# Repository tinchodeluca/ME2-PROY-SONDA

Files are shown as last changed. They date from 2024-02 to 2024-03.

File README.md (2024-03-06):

# Cálculo de Permitividad de Materiales mediante una Sonda

Este proceso permite calcular la permitividad relativa (εᵣ) de materiales a partir de la medición de parámetros S11 con un VNA y una sonda. Se adquieren los parámetros de circuito abierto, circuito cerrado y agua destilada como referencia, y luego se miden los parámetros del material a calcular.
___
## Catedra Medidas Electrónicas II - UTN FRBA - 2023 -
>>**Revisión 01**  Fecha: 05/03/2024
***
- **Docente:** Henze Alejandro Martín
- **JTP    :** Geria Juan Manuel
### Alumnos 
- Almude Tupac
- De Luca Martín Alexandro
  
Se partió de trabajos de años anteriores para la misma cátedra que se encuentran [en la siguiente ruta](./01-Bibliografía/Antecedentes%20Soft/Sonda%20Open%20Ended%20-%20Antecedentes).
___
## Contenido

1. [Modelo de Sonda](#modelo-de-la-sonda-utilizada)
2. [Funciones Implementadas](#funciones-implementadas)
    - [Procesamiento de archivos S1P obtenidos del VNA](#procesamiento-de-archivos-s1p-obtenidos-del-vna)
    - [Conversión a Coordenadas Rectangulares](#conversión-a-coordenadas-rectangulares)
    - [Conversión de parámetros S11 a Y11](#conversión-de-parámetros-s11-a-y11)
    - [Submuestreo de S11 (SUBsample_S11)](#submuestreo-de-s11-subsamples11)
    - [Remuestreo de S11 (Resample_S11)](#remuestreo-de-s11-resamples11)
    - [Obtención de Constante Dieléctrica Relativa (εᵣ) del DUT en Medio Agua](#obtención-de-constante-dieléctrica-relativa-εᵣ-del-dut-en-medio-agua)
    - [Obtención de Conductancia en Función de la Frecuencia con el Setup Calibrado](#obtención-de-conductancia-en-función-de-la-frecuencia-con-el-setup-calibrado)
3. [Modelos Teóricos](#modelos-teóricos)
    - [Obtención de Modelo de Debye para Agua Destilada](#obtención-de-modelo-de-debye-para-agua-destilada)
    - [Obtención de Modelo de Constante Dieléctrica para Alcohol Etílico](#obtención-de-modelo-de-constante-dieléctrica-para-alcohol-etílico)
    - [Obtención de Modelo de Constante Dieléctrica para Alcohol Isopropílico](#obtención-de-modelo-de-constante-dieléctrica-para-alcohol-isopropílico)
4. [Ejemplos de Uso](#ejemplos-de-uso)
    - [Procesamiento de Archivos S1P para Medios Específicos](#procesamiento-de-archivos-s1p-para-medios-específicos)
    - [Obtención de Constante Dieléctrica Relativa para Diferentes Medios](#obtención-de-constante-dieléctrica-relativa-para-diferentes-medios)
    - [Procesamiento y Estimación de Constante Dieléctrica Relativa para Resina](#procesamiento-y-estimación-de-constante-dieléctrica-relativa-para-resina)
5. [Proceso de Clonación y Procesamiento en Python](#proceso-de-clonación-y-procesamiento-en-python)
6. [Pasos a Seguir](#pasos-a-seguir)
7. [Resultados](#resultados)
    - [Imágenes de Permitividad Relativa (εᵣ)](#imágenes-de-permitividad-relativa-εᵣ)
        - [Er_Acetona_Medido](#er_acetona_medido)
        - [Er_agua_Teorico](#er_agua_teorico)
        - [Er_AlchEtilico_Teorico](#er_alchetilico_teorico)
        - [Er_AlchIsoprop_Medido](#er_alchisoprop_medido)
        - [Er_AlchIsoprop_Teorico](#er_alchisoprop_teorico)
        - [Er_AlchIsoprop_VS](#er_alchisoprop_vs)
        - [Er_Resina](#er_resina)
___
## Modelo de la Sonda utilizada

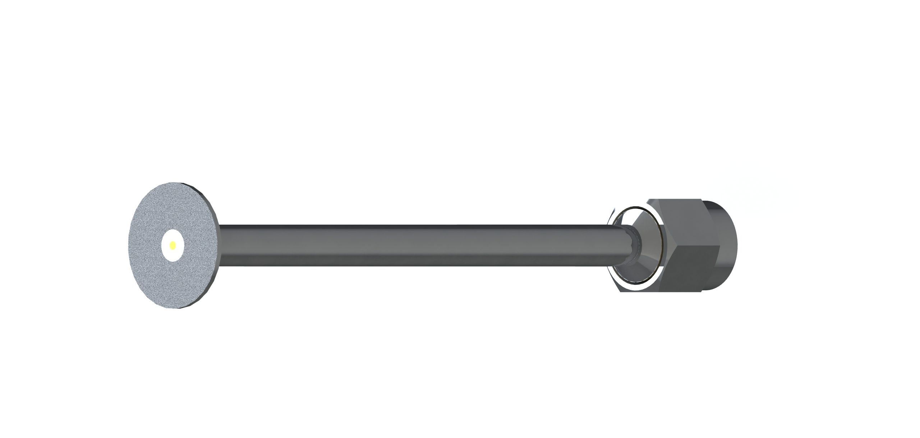
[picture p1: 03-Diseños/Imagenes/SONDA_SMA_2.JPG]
Imagen de la Sonda


Se pueden encontrar los [modelos 3D](./03-Diseños/Sonda/) de la sonda utilizada y las simulaciones en CST con dicha sonda en la [la siguiente carpeta](./04-CST/)
***
# Funciones implementadas
## Procesamiento de archivos S1P obtenidos del VNA
La función `def vna_proc_file(file_path, file_name)` se encarga de procesar los archivos seleccionados y devuelve un diccionario con la información extraída. Los archivos S1P pueden estar en formato de Modulo y Fase o Parte Real e Imaginaria, dependiendo del modo de adquisición del VNA.

- #### Parámetros
    - `file_path:` Ruta del archivo.
    - `file_name:` Nombre del archivo.
- #### Retorno
    Un diccionario con las siguientes claves:
    - `'Date':` Fecha del archivo.
    - `'Data':` Información de las primeras 11 líneas del archivo.
    - `'Index':` Encabezados de las columnas de datos.
    - `'Frec':` Lista de frecuencias extraídas del archivo.
    - `'Complex':` Lista de números complejos correspondientes a los datos procesados.

Si el archivo tiene extensión `.csv`, la función imprimirá un mensaje indicando que el formato CSV no está soportado y retornará sin procesar el archivo.

## Conversión a Coordenadas Rectangulares

La función `def convertir_a_rectangular(modulo_db, fase_grados)` convierte las coordenadas polares (módulo en decibelios y fase en grados) a coordenadas rectangulares.

- #### Parámetros
    - `modulo_db`: Módulo en decibelios.
    - `fase_grados`: Fase en grados.

- #### Retorno
    - Un número complejo en coordenadas rectangulares.

## Conversión de parámetros S11 a Y11

La función `def S11_to_Y11(frec, S11)` convierte los parámetros S11 (coeficiente de reflexión) a parámetros Y11 (parámetros admitancia).

- #### Parámetros
    - `frec`: Frecuencia.
    - `S11`: Coeficiente de reflexión S11.

- #### Retorno
    Un diccionario con las siguientes claves:
    - `'Frec'`: Frecuencia.
    - `'Complex'`: Valor complejo correspondiente a Y11.

Estas funciones proporcionan herramientas esenciales para el procesamiento y análisis de archivos S1P obtenidos del VNA.
## Submuestreo de S11 (SUBsample_S11)

La función `def SUBsample_S11(small_dict, big_dict)` realiza un submuestreo de los datos en `big_dict` para que coincidan con las frecuencias presentes en `small_dict`. La función elimina las frecuencias no presentes en `small_dict` y retorna un nuevo diccionario con el conjunto de datos ajustado.

- #### Parámetros
  - `small_dict`: Diccionario con un conjunto de datos más pequeño.
  - `big_dict`: Diccionario con un conjunto de datos más grande.

- #### Retorno
  Un nuevo diccionario con las siguientes claves:
  - `'Frec'`: Lista de frecuencias ajustadas.
  - `'Complex'`: Lista de números complejos ajustados.

La función imprimirá un mensaje si el diccionario más pequeño no tiene menos elementos que el diccionario más grande.

- #### Ejemplo de uso
  ```python
  result_dict = SUBsample_S11(small_dict, big_dict)
  ```

## Remuestreo de S11 (Resample_S11)

La función `def Resample_S11(smaller_set, data)` realiza un remuestreo de los datos en `data` para que coincidan con las frecuencias presentes en `smaller_set`. La función realiza una interpolación lineal entre los puntos de datos existentes y devuelve un nuevo conjunto de datos con las frecuencias ajustadas.

- #### Parámetros
  - `smaller_set`: Diccionario con un conjunto de datos más pequeño.
  - `data`: Diccionario con un conjunto de datos más grande.

- #### Retorno
  Un nuevo diccionario con las siguientes claves:
  - `'Frec'`: Lista de frecuencias ajustadas.
  - `'Complex'`: Lista de números complejos ajustados.

- #### Ejemplo de uso
  ```python
  resampled_data = Resample_S11(smaller_set, data)
  ```

## Obtener Constante Dieléctrica Relativa (εᵣ) del Dispositivo bajo Prueba (DUT) en Medio Agua

La función `def get_er_DUTm(frecs, S11_medido, S11_agua, S11_aire, S11_corto)` calcula la constante dieléctrica relativa (εᵣ) del Dispositivo bajo Prueba (DUT) en medio acuoso. Se utiliza un modelo de Debye para el agua en la estimación.

- #### Parámetros
    - `frecs`: Lista de frecuencias.
    - `S11_medido`: Parámetro de dispersión medido del DUT.
    - `S11_agua`: Parámetro de dispersión medido en agua.
    - `S11_aire`: Parámetro de dispersión medido en aire.
    - `S11_corto`: Parámetro de dispersión medido en un cortocircuito.

- #### Retorno
    - Valor numérico de la constante dieléctrica relativa (εᵣ) del DUT en medio acuoso.

## Obtener Conductancia en Función de la Frecuencia con el Setup Calibrado

La función `def get_er_setup(frecs, S11_medido, s11_agua, s11_abierto, s11_isopropilico, s11_corto)` calcula la conductancia en función de la frecuencia con el setup calibrado. Se realiza una estimación de la constante dieléctrica relativa del agua y del isopropanol.

- #### Parámetros
    - `frecs`: Lista de frecuencias.
    - `S11_medido`: Parámetro de dispersión medido del DUT.
    - `s11_agua`: Parámetro de dispersión medido en agua.
    - `s11_abierto`: Parámetro de dispersión medido en un circuito abierto.
    - `s11_isopropilico`: Parámetro de dispersión medido en isopropanol.
    - `s11_corto`: Parámetro de dispersión medido en un cortocircuito.

- #### Retorno
    - Lista de valores numéricos que representan la conductancia en función de la frecuencia con el setup calibrado.

Ambas funciones proporcionan herramientas para el análisis de parámetros de dispersión y la estimación de constantes dieléctricas relativas en diferentes entornos.
# Modelos Teóricos
## Obtener Modelo de Debye para Agua Destilada

La función `def get_debye_model(frecs): #Patron agua destilada` devuelve el modelo de Debye para la constante dieléctrica relativa del agua destilada.

- #### Parámetros
    - `frecs`: Lista de frecuencias.

- #### Retorno
    - Lista de valores numéricos que representan la constante dieléctrica relativa del agua destilada en función de la frecuencia.

## Obtener Modelo de Constante Dieléctrica para Alcohol Etílico

La función `def get_er_pat_alc_etilico(frecs)` proporciona el modelo de la constante dieléctrica relativa para el alcohol etílico.

- #### Parámetros
    - `frecs`: Lista de frecuencias.

- #### Retorno
    - Lista de valores numéricos que representan la constante dieléctrica relativa del alcohol etílico en función de la frecuencia.

## Obtener Modelo de Constante Dieléctrica para Alcohol Isopropílico

La función `def get_er_pat_alc_isopropilico(frecs)` devuelve el modelo de la constante dieléctrica relativa para el alcohol isopropílico al 99% según la curva de Debye.

- #### Parámetros
    - `frecs`: Lista de frecuencias.

- #### Retorno
    - Lista de valores numéricos que representan la constante dieléctrica relativa del alcohol isopropílico en función de la frecuencia.

Estas funciones proporcionan modelos para estimar la constante dieléctrica relativa en diferentes medios, lo que puede ser útil en el análisis de parámetros de dispersión en entornos específicos.
## Ejemplos de Uso

#### Procesamiento de Archivos S1P para Medios Específicos

```python
mea_date = '22-02-24'
file_path = './ME2-PROY-SONDA/rsc/' + mea_date + '/'

# files[mea_date][0] #Aire
# files[mea_date][1] #Isopropil
# files[mea_date][2] #Agua destilada
# files[mea_date][3] #Corto circuito
# files[mea_date][4] #Acetona

s11_agua_dest = vna_proc_file(file_path, files[mea_date][2])
s11_short     = vna_proc_file(file_path, files[mea_date][3])
s11_aire      = vna_proc_file(file_path, files[mea_date][0])
s11_isop      = vna_proc_file(file_path, files[mea_date][1])
s11_acetona   = vna_proc_file(file_path, files[mea_date][4])
```

#### Obtener Constante Dieléctrica Relativa para Diferentes Medios

```python
frecs      = s11_agua_dest['Frec']
er_iso     = get_er_DUTm(frecs, s11_isop['Complex'], s11_agua_dest['Complex'], s11_aire['Complex'], s11_short['Complex'])
er_agua    = get_er_DUTm(frecs, s11_agua_dest['Complex'], s11_agua_dest['Complex'], s11_aire['Complex'], s11_short['Complex'])
er_acetona = get_er_DUTm(frecs, s11_acetona['Complex'], s11_agua_dest['Complex'], s11_aire['Complex'], s11_short['Complex'])
```

#### Procesamiento y Estimación de Constante Dieléctrica Relativa para Resina
*(utilizando un set de datos mayor con una calibración de menor tamaño, interpolando y muestreando nuevamente)*

```python
file_path = './ME2-PROY-SONDA/rsc/' + '21-12-23/'
file_name = 'ResinaN.s1p'
s11_resina_temp = vna_proc_file(file_path, file_name)
s11_resina = Resample_S11(s11_acetona, s11_resina_temp)
er_resina  = get_er_DUTm(frecs, s11_resina['Complex'], s11_agua_dest['Complex'], s11_aire['Complex'], s11_short['Complex'])
```

Estos ejemplos ilustran cómo procesar archivos S1P para diferentes medios y calcular la constante dieléctrica relativa en función de la frecuencia para cada medio. Además, se muestra cómo aplicar el proceso a un nuevo conjunto de datos (Resina) utilizando una función de resample para ajustar las frecuencias.
## Proceso de Clonación y Procesamiento en Python

El script Python ubicado en la carpeta **`05-Software`** de este repositorio utiliza Google Colab o Jupyter para realizar un `git clone` del repositorio y procesar los archivos, almacenándolos en una lista. El script se puede encontrar en [este archivo](./05-Software/ME2_PROYECTO_2023.ipynb).

### Descripción del Proceso

1. **Clonación del Repositorio:**
   - El script comienza realizando un `git clone` del repositorio para obtener la última versión de los archivos.

     ```python
     !git clone https://github.com/tinchodeluca/ME2-PROY-SONDA.git
     ```

2. **Procesamiento de Archivos:**
   - Luego, el script explora la carpeta `./ME2-PROY-SONDA/rsc/` y almacena en un diccionario la lista de archivos para cada carpeta.

     *_([la carpeta recursos `rsc`](./rsc/) almacena carpetas con la fecha de medición y dentro de cada una las señales adquiridas oportunamente)_*

     ```python
     file_path = './ME2-PROY-SONDA/rsc/'
     files = {}

     for folder in os.listdir(file_path):
       if os.path.isdir(file_path + '/' + folder ):
         file_names = os.listdir( file_path + '/' + folder + '/' )
         files[folder] = file_names
     ```
## Pasos a Seguir:

1. **Medición de Parámetros de Referencia:**
   - Medir y almacenar los parámetros S11 del **circuito abierto**.
   - Medir y almacenar los parámetros S11 del **circuito cerrado**.
   - Medir y almacenar los parámetros S11 del **agua destilada**.

2. **Procesamiento de Datos de Referencia:**
   - Procesar los archivos S1P de los parámetros medidos para obtener información estructurada.
   - Calcular la constante dieléctrica relativa (εᵣ) para el **circuito abierto**, el **circuito cerrado** y el **agua destilada** utilizando las funciones implementadas.

3. **Medición de Parámetros del Material a Calcular:**
   - Medir y almacenar los parámetros S11 del material cuya permitividad se desea calcular.
   - Almacenar los documentos en la [carpeta de recursos](./rsc/) junto con el resto de señales.

4. **Procesamiento de Datos del Material a Calcular:**
   - Procesar el archivo S1P del material para obtener información estructurada.
   - Calcular la constante dieléctrica relativa (εᵣ) del material utilizando las funciones implementadas.

5. **Resultados y Análisis:**
   - Analizar los resultados obtenidos para determinar la permitividad relativa del material en función de la frecuencia.
   - Documentar y presentar los resultados de manera clara y comprensible.

Este proceso brinda una metodología ordenada y eficiente para calcular la permitividad relativa de materiales mediante una sonda, permitiendo un análisis detallado y una presentación organizada de los resultados.

## Resultados

## Imágenes de Permitividad Relativa (εᵣ)

### Er_Acetona_Medido
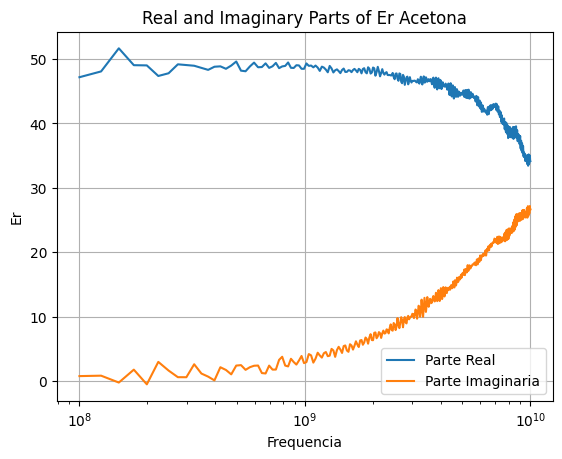
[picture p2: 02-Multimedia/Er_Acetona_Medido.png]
Er_Acetona_Medido


### Er_agua_Teorico
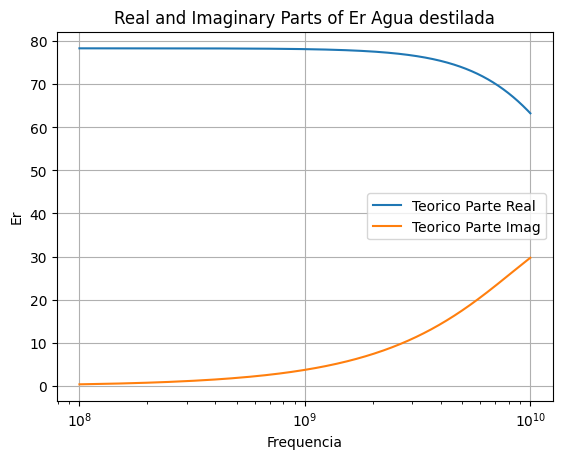
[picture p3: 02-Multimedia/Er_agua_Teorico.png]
Er_agua_Teorico


### Er_AlchEtilico_Teorico
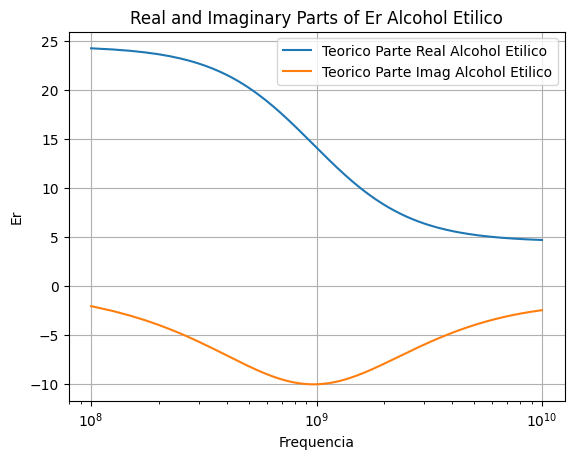
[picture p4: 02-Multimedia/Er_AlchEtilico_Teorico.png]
Er_AlchEtilico_Teorico


### Er_AlchIsoprop_Medido
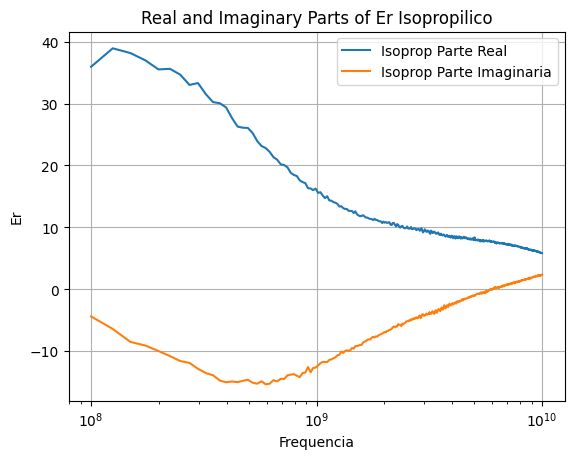
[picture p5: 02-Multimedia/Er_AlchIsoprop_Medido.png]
Er_AlchIsoprop_Medido


### Er_AlchIsoprop_Teorico
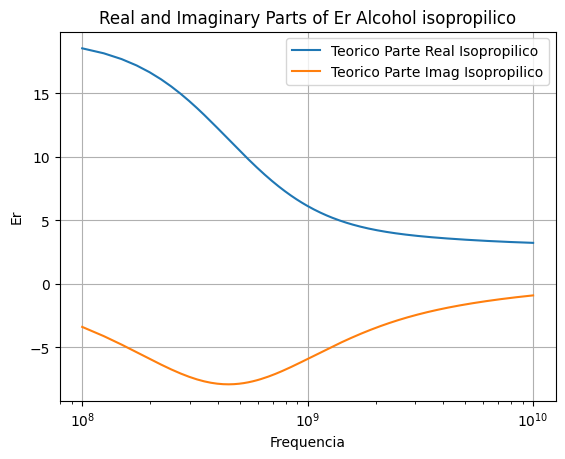
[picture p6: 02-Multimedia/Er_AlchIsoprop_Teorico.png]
Er_AlchIsoprop_Teorico


### Er_AlchIsoprop_VS
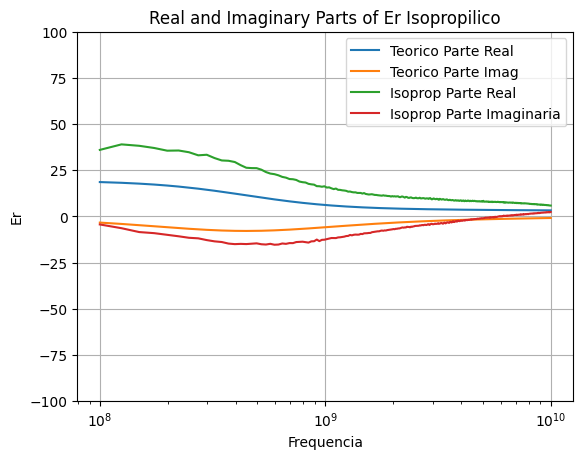
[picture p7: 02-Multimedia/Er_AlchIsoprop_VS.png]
Er_AlchIsoprop_VS


### Er_Resina
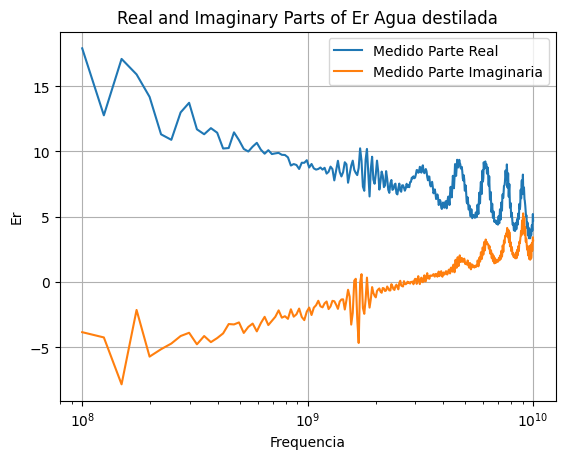
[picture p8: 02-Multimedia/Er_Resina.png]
Er_Resina


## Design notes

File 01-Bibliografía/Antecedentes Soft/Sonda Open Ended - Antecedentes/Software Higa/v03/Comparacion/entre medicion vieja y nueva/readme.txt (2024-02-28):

Comparacion de las mediciones OLD (VNA UTN FRBA) y NEW (VNA INTI)
=================================================================

- Comparacion solo con las temperaturas OLD: 25, 40, 55 y 60.

- Modificacion "." por "," de los archivos .s1p para que el excel interprete correctamente los numeros.

- Eliminacion de la linea de parametros del archivo .s1p.

- Modificacion de rangos:
	- OLD: 100MHz-3GHz (pasos de 50MHz) -> 100MHz-3GHz (pasos de 50MHz y 100MHz a partir del GHz) 
	- NEW: 300kHZ-4GHZ (pasos de 10MHz y 100MHz a partir del GHz) -> 100MHz-3GHz (pasos de 50MHz y 100MHz a partir del GHz)

- Formato de OLD:
	- Frecuencia [Hz]
	- Magnitud s11
	- Fase s11 en grados

- Formato de NEW:
# Hz S RI R 50.000000
	- Frecuencia [Hz]
	- Parametros S
	- Formato: real-imaginario.
	- Resistencia referencia: 50ohm

- Modificacion  del formato de OLD para obtener en vez de magnitud y fase, parte real e imaginaria.

- Modificacion  del formato de NEW para mostrar el formato del numero en tipo general.

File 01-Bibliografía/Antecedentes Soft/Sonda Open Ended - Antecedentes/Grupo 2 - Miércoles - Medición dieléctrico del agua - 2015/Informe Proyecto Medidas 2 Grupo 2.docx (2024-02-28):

UNIVERSIDAD TECNOLÓGICA NACIONAL

FACULTAD REGIONAL BUENOS AIRES

Departamento de Electrónica

Materia: Medidas Electrónicas 2

# Proyecto: MEDICIÓN DE PERMITIVIDAD ELÉCTRICA EN LÍQUIDOS CON PARÁMETROS S

Docente: Ing. Alejandro Henze

Jefe de TP: Ing. Guillermo Monasterios

Ayudante de TP: Ing. Nahir Murana

Grupo N°: 2

Alumnos :

| Apellido y Nombre | Legajo
1 | Das, Ariel | 120.214-5
2 | Cismondi, Luciano | 134.658-1
3 | Grass, Pablo | 111659-9
4 | Higa, Déborah | 143.126-2

Entrega Informe | Fecha | Firma
Primer entrega | / / 12
Aprobación | / / 12

Entrega | Devolución | Re-entrega | Firma Recepción
2° | / / 12 | / / 12
3° | / / 12 | / / 12
4° | / / 12 | / / 12

MEDICIÓN DE PERMITIVIDAD ELÉCTRICA EN LÍQUIDOS CON PARÁMETROS S

Cismondi L., Das A., Grass P., Higa D.

Docente a cargo: Ing. Alejandro Henze

Universidad Tecnológica Nacional - Facultad Regional Buenos Aires

Medidas Electrónicas 2

Resumen: La caracterización de las propiedades dieléctricas de los materiales a frecuencia de radio ha ganado cada vez más importancia, en especial en los campos de investigación en circuitos de microondas, ya que permite obtener resultados del comportamiento eléctrico y/o magnético del material. El siguiente proyecto consiste en la medición de la permitividad eléctrica en líquidos con parámetros S a través de una sonda coaxial.

# 1. INTRODUCCIÓN

La medición de las propiedades dieléctricas implica caracterizaciones de la relación entre la permitividad relativa (εr) y la permeabilidad relativa (μr) de los materiales.

La permitividad dieléctrica se compone de una parte real y una parte imaginaria:

• La parte real, se conoce como constante dieléctrica. Es una medida de la cantidad de energía almacenada en el material, producto de un campo eléctrico externo.

• La parte imaginaria, se conoce como factor de pérdida. Es una medida de la cantidad de energía disipada.

El término tang(ɣ) representa la relación entre la parte imaginaria y la real, llamada tangente de pérdida o factor de disipación[1].

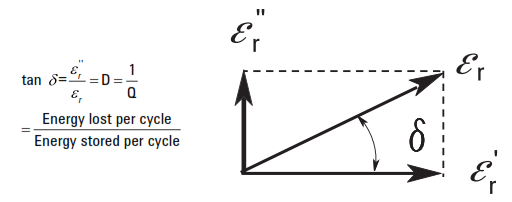
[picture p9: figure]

Fig.1. Representación gráfica del factor de disipación y sus componentes.

La permeabilidad relativa también consta de una parte real, que representa la cantidad de energía almacenada debido a un campo magnético; mientras que la parte imaginaria representa las pérdidas magnéticas del material. La medición de la permeabilidad solo es aplicable a los materiales magnéticos, siendo la mayoría no magnéticos, la permeabilidad es muy cercana a la del espacio libre.

## Distintos métodos de medición

Muchos métodos han sido desarrollados, cada uno se limita a frecuencias específicas, materiales y aplicaciones. El avance de la tecnología ha permitido utilizar programas e instrumentos que facilitan la obtención de los parámetros de transmisión y reflexión. Entre los procedimientos destacados se pueden encontrar: Método de la línea de transmisión/reflexión, método espacio libre, método por resonancia y método por sonda coaxial, siendo este último el utilizado en este proyecto[2].

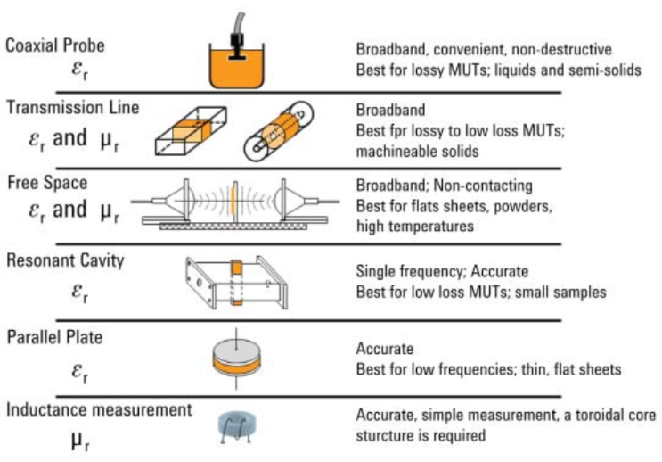
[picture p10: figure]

Fig.2. Distintos métodos y sus aplicaciones.

# 2. DESARROLLO DEL TRABAJO

## Método por sonda coaxial

Ventajas:

• No requiere mecanizado del material bajo ensayo.

• Luego de la calibración, la repetitividad del ensayo es elevada.

• La medición puede realizarse en un ambiente de temperatura controlada.

Desventajas:

• Solo puede medir el parámetro de reflexión.

• Se ve afectada por gaps de aire entre la sonda y la muestra.

El método consiste en la utilización de un cable coaxial como material por donde propagar la señal y se realiza utilizando tres herramientas:

• Vector Network Analyzer (VNA): Realiza la medición del parámetro S11 en función de las frecuencias programadas. Consiste en un generador de señal que excita a una determinada frecuencia al dispositivo bajo prueba (MUT, Material Under Test). El Receptor sintonizado a dicha frecuencia, detecta las señales transmitida y reflejada del MUT y el Display muestra el módulo y la fase de la transmisión y reflexión en función de la frecuencia.

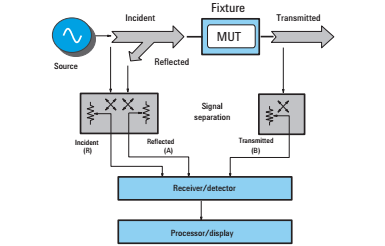
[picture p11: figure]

Fig.3. Setup del VNA utilizado (en nuestro caso, sin medir (B)).

De esta manera, permite la medición de los parámetros S, siendo el de interés el parámetro S11, el coeficiente de reflexión de la tensión del puerto de entrada.

• Sonda: cable coaxial abierto (“open-ended”) utilizado como transductor para la medición de la permitividad de un material. Se llena el coaxial con el material líquido, provocando un cambio en los campos eléctricos y magnéticos en el coaxial y permitiendo así relacionar la medición del parámetro S11 con la permitividad del material.

• Software: convierte el parámetro S11 obtenido de la medición en la permitividad. Se realiza a través de algoritmos iterativos.

## VNA (Vector Network Analyzer)

EL VNA utilizado no era un instrumento stand alone. El mismo fue realizado por los ayudantes de cátedra, y estaba constituido por un generador de RF (Agilent), un osciloscopio (Agilent) y un acopador direcciconal (Agilent).
El generador de RF genera la señal a inyectar por el puerto. El acoplador direccional separara señal incidente y reflejada del puerto del VNA para poder ser medida por dos canales analógicos del osciloscopio.

El control de ambos instrumentos (generación y medición) estaba hecho a través de una computadora, la cual mediante un software codificado en LabView (IDE), generaba los barridos de frecuencia programables, media señal incidente y reflejada, y calculaba mediante procesamiento los parámetros S del puerto.

El sistema descrito fue provisto por la Facultad (UTN FRBA).

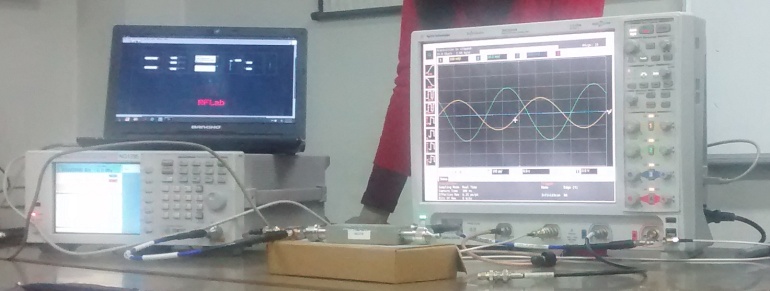
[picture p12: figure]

Fig.4. Vista global del setup VNA.

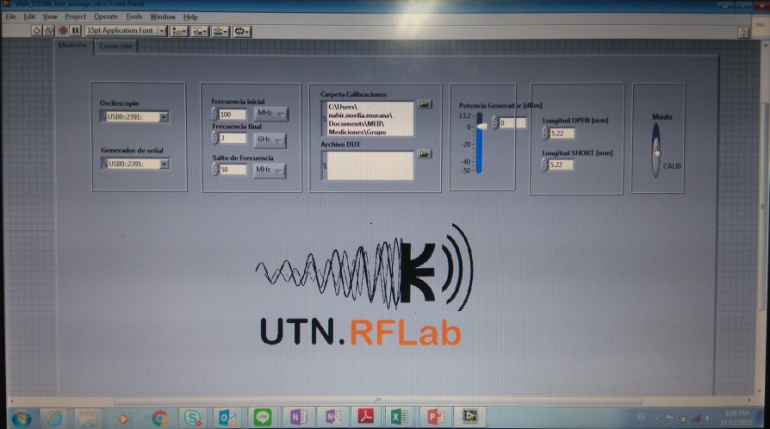
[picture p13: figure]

Fig.5. Vista del control del VNA (IDE LabView)

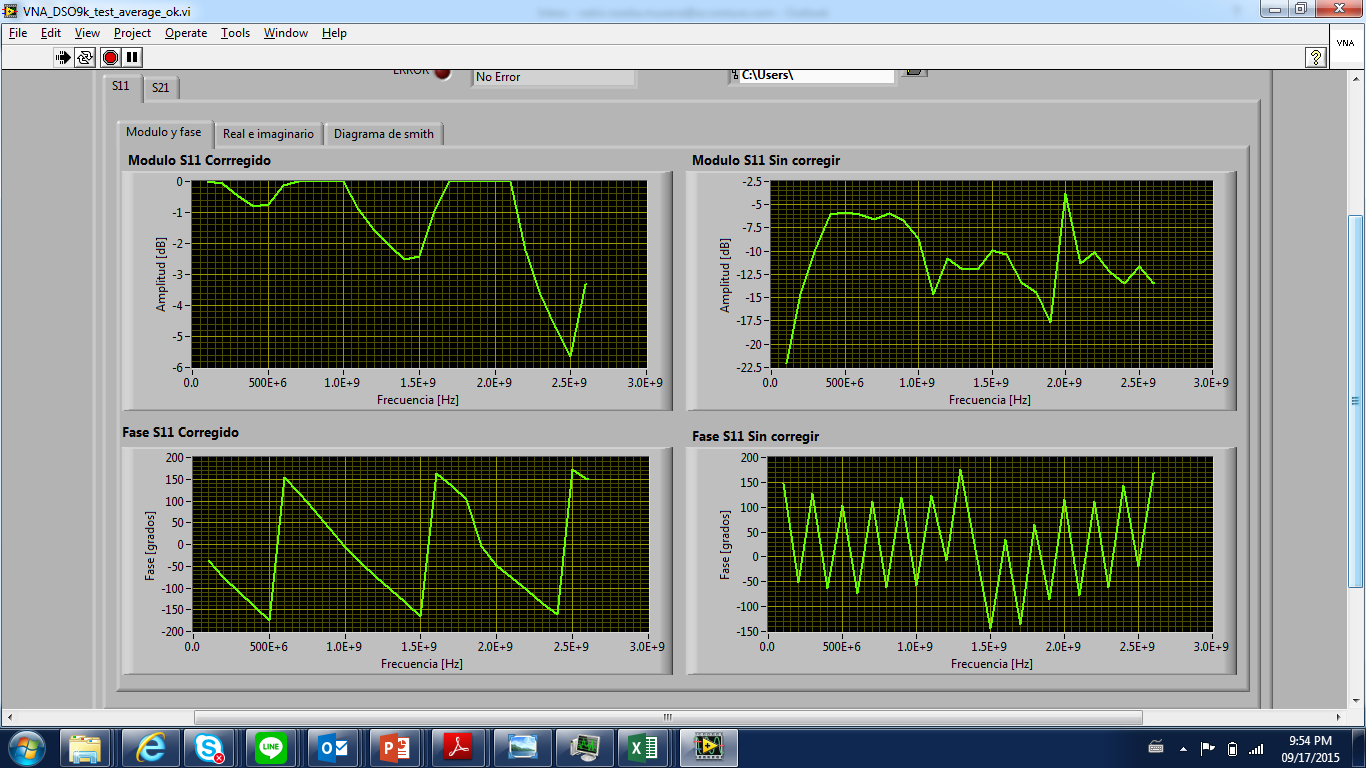
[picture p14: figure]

Fig.6. Pantalla de resultados obtenidos en una medición con el VNA.

## Construcción de la sonda

La mecanización de la sonda se realizó teniendo en cuenta la impedancia característica del sistema a 50Ω con un dieléctrico de aire. Además era primordial prestar atención a la necesidad de poder introducir un líquido dentro de la sonda para que actúe como dieléctrico.

Se construyó una sonda de cobre de un diámetro exterior suficiente para que pueda alojar un conector tipo N en una de sus extremos. Además, la varilla de cobre más fina que se consiguió era de 8mm de diámetro, así que nos fijaba la dimensión “d”, lo que nos deja calcular D:

Zo=1/(2.π.σ).ln(D/d)=(η_0)/(2.π).ln(D/d)

Zo=(120.πΩ)/(2.π).ln((18,4)/8)=50Ω

Otro tema a resolver es que dadas las dimensiones del conector tipo N y su dieléctrico se adaptó el extremo del conducto central al pin central del conector, siempre manteniendo la relación de diámetros para mantener la impedancia característica.

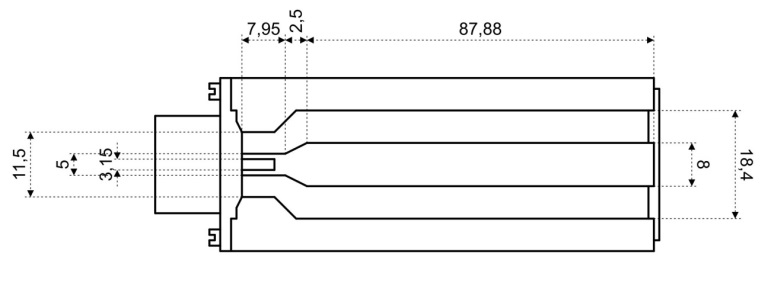
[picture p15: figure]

Fig.7. Plano de la sonda construida [mm].

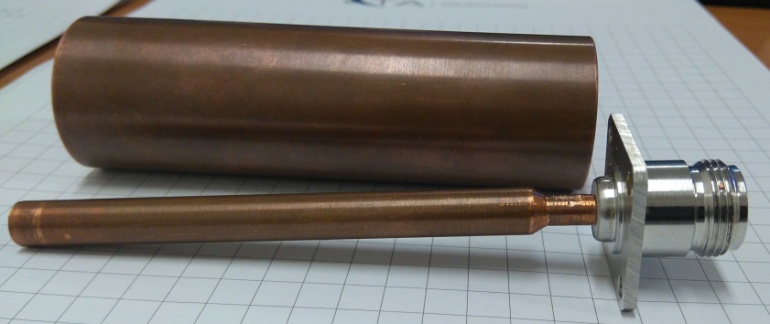
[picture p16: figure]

Fig.8. Vista lateral de los conductores de la sonda.

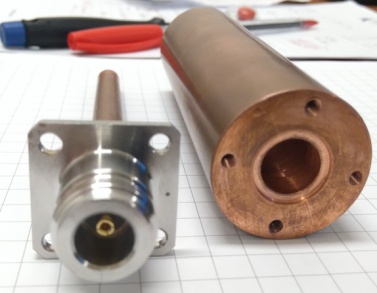
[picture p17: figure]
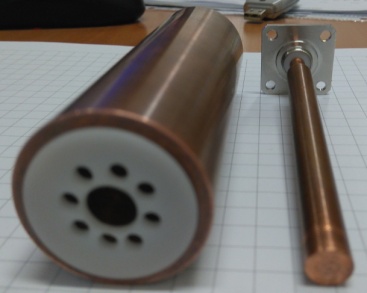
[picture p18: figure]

Fig.9. Vistas posterior e inferior de la sonda.

## Método de conversión

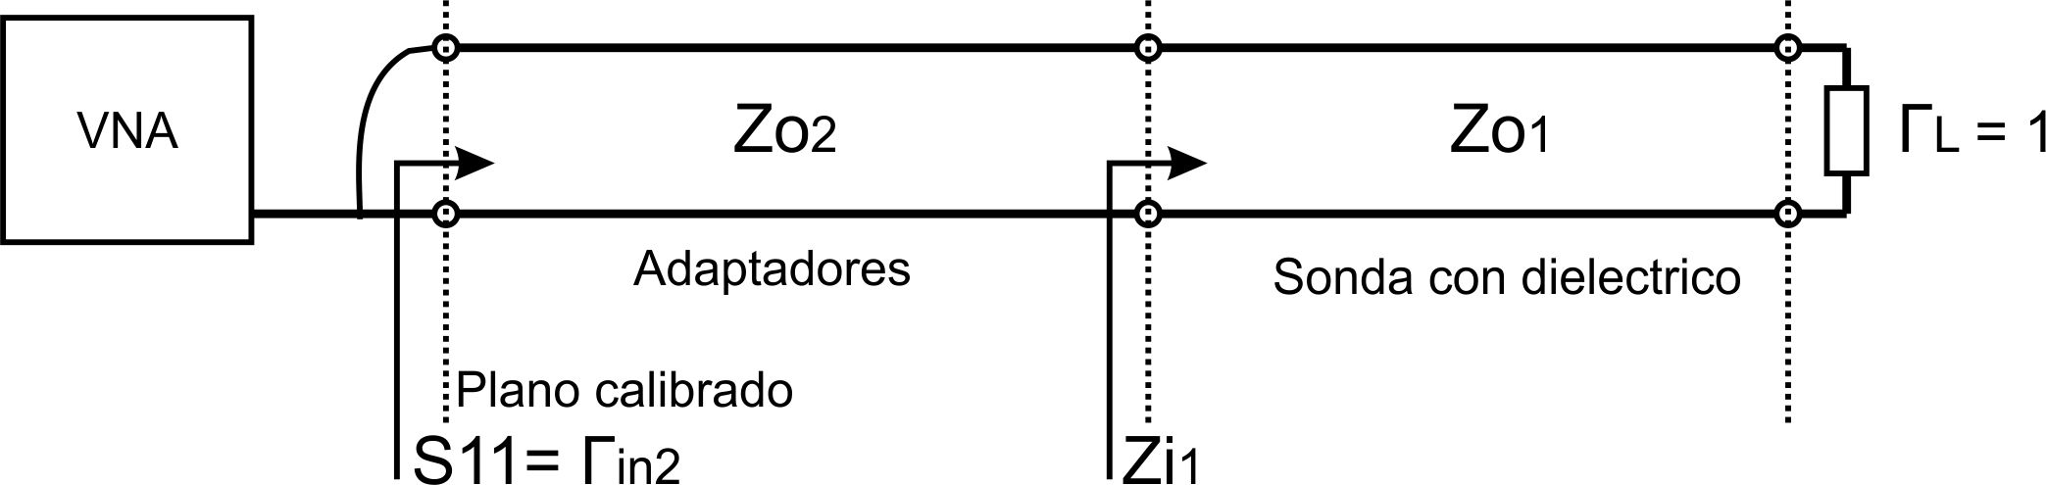
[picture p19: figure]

Fig.10. Setup de medición utilizado.

El plano que figura como “calibrado”, es el punto donde se realizó la calibración del VNA con el método OSM.

Partiendo de la medición del S11:

Γin_2 =s_11

Zi_2 =Zo_2 (1+Γin_2)/(1-Γin_2)

Zi_1 =(j(Zo_2 )^2 .tg(β_2 l_2 )-Zi_2 Zo_2)/(jZi_2 .tg(β_2 l_2 )-Zo_2)

Zi_1 =(1/(2π)√((μ_0)/(ϵ_0 ϵ^(*))).ln⁡(b/a))/(jtg((2π√(ϵ^(*)).f.l_1)/c))

Donde igualando las dos últimas ecuaciones, se puede resolver iterativamente el ϵ^(*) (ya que el mismo esta dentro de una función tangente).

## Resolución de las ecuaciones por software

Nuestra ecuación a resolver es:

0=(1/(2π)√((μ_0)/(ϵ_0 ϵ^(*))).ln⁡(b/a))/(jtg((2π√(ϵ^(*)).f.l_1)/c))-Zi_1

Para resolver la ecuación no lineal de incógnita compleja se utilizó la función fsolve de la librería scipy de Python. También podría usarse la función con el mismo nombre pero de Matlab. Ambas buscan las raíces de una ecuación pero mediante distintos algoritmos: en el caso de Python, utiliza MINPACK’shybrdyhybrj; y en el caso de Matlab, se puede elegir entre tres opciones: 'trust-region-dogleg','trust-region-reflective' y 'levenberg-marquardt'.

fsolve recibe como parámetros obligatorios la ecuación a resolver y un valor estimado de las raíces. Este último parámetro es importante por dos razones:

1) Desde este punto empieza a iterar hasta llegar al resultado, sino a determinada cantidad de iteraciones la función devuelve el último resultado al que llegó e indica que no logró converger.
2) Nuestra ecuación tiene infinitas soluciones. Esto se puede observar desde una perspectiva de una variable donde las soluciones son las intersecciones gráficas entre una tangente y una hipérbola.

Por lo tanto, es importante conocer los valores teóricos y proporcionárselos a la función para que no diverja y para que no caiga en soluciones locales no deseadas. Para ello, recurrimos al modelo de Debye:

ϵ^(*) =ϵ_(∞) +(ϵ_S -ϵ_(∞))/(1+jωτ)

ϵ_(∞) :permitividad relativa a alta frecuencia.

ϵ_S :permitividad relativa a la frecuencia 0 (estática).

τ:tiempo de relajación.

Tanto ϵ_S como τ son inversamente proporcionales a la temperatura. Basándonos en [4] obtuvimos los valores empíricos para cada frecuencia y temperatura del agua destilada, que se detallaran en la parte de mediciones.

# 3. RESULTADOS

## Agua destilada

Fig.11. Comparación tangente de perdida teórica y medida @26º.

Fig.12. Comparación tangente de perdida teórica y medida @40º.

Fig.13. Comparación tangente de perdida teórica y medida @54º.

Fig.14. Comparación tangente de perdida teórica y medida @60º.

Fig.15. Comparación constante dieléctrica teórica y medida @26º.

Fig.16. Comparación constante dieléctrica teórica y medida @40º.

Fig.17. Comparación constante dieléctrica teórica y medida @54º.

Fig.18. Comparación constante dieléctrica teórica y medida @60º.

## Aire

Fig.19. Constante dieléctrica a @26º.

Fig.20. Factor de perdida a @26º.

Fig.21. Tangente de perdida a @26º.

## Alcohol

Fig.22. Constante dieléctrica a @26º.

Fig.23. Factor de perdida a @26º.

Fig.24. Tangente de perdida a @26º.

# 4. DISCUSIÓN

Comparando las mediciones obtenidas, con los valores teóricos calculados, podemos notar tres tendencias significativas.
La primera es que las mediciones tienen un alto valor de dispersión. Consideramos que es debido al error de método de medición (configuración mecánica de la sonda, VNA, agua utilizada) ya que se puede observar que para todas las mediciones a diferentes temperaturas, la forma de los datos en función de la frecuencia se repite sistemáticamente.

La segunda, es que a frecuencias mayores que 1GHz la curva teórica del agua tiende a aumentar, y las mediciones tienen a disminuir.

Esto es debido a la frecuencia de corte de la sonda. Si la calculamos, tomando la fórmula para un cable coaxial y considerando el épsilon del agua y dimensiones de la misma:

f_C _([GHz]) =(190,5)/(√(ε_r)(D+d)_([mm]))=(190,5)/(√81(18,4+8)_([mm]))=0.803[GHz]

Podemos ver que el valor teórico es cercano a la frecuencia donde notamos que la curva empieza a decrecer en vez de subir.

La tercera y más importante, es que a frecuencias comprendidas entre 100MHz y 1GHz y pese a la dispersión, el valor medio de la curva medida, sigue a la curva teórica. Inclusive comparamos el valor medio de la parte real (constante dieléctrica) con valores obtenidos en [5] y resultan bastante similares.
Además, la sonda en su configuración original, tenía un fino anillo de teflón en su punta abierta para mantener la coaxialidad de los conductores. Esto trae aparejado dos problemas. Uno, que en los cálculos teóricos se tomaba como carga de la sonda una carga abierta, sin considerar los problemas de borde para el campo electromagnético. El segundo es que en realidad, dicho anillo de teflón debería considerarse como carga de la sonda, siendo este un capacitor coaxial a calcular y contemplar en los cálculos.

5. CONCLUSIONES

Con respecto a la sonda, fue un buen primer prototipo, pero se debe rediseñarla.

Primero, que la misma tenga un conector tipo N macho, tal cual tienen los patrones OSM que utilizamos y no agregar elementos a la incertidumbre de medición, como ser adaptadores.

Segundo, hay que rediseñar las dimensiones “D y d” de acuerdo a una frecuencia de corte de 3 o 3.5GHz con un ε_r =81 (agua) y que mantenga una Z_o =50Ω para el aire.

Desarrollo:

f_C _([GHz]) =(190,5)/(√(ε_r)(D+d)_([mm])) Zo =60/(√(ε_r))ln(D/d)

Despejando de cada ecuación,

(D+d)_([mm]) =(190,5)/(√(ε_r) f_C _([GHz])) (D/d)=e^((Zo√(ε_r))/60)

(D+d)_([mm]) =K_2 (1) (D/d)=K_1 (2)

K_1 se obtiene calculando y considerando:

Zo=50Ω y ε_r =1 (aire) →K_1 =2,301

Y K_2 lo tenemos que calcular considerando:

f_C _([GHz]) =3.2 y ε_r =81 (Agua), →K_2 =6,6146

Despejando D de (2) y sustituyendo en (1),

K_1 .d+d=K_2 → d(1+K_1 )=K_2 → d=(K_2)/(1+K_1)

en (2)→K_1 (K_2)/(1+K_1)

Finalmente reemplazando los valores calculados de las constantes:

d=2,0038mm y D=4,6108mm

Como se puede observar, las dimensiones son bastante chicas y plantea un desafío mecánico a la hora de construir la sonda.

Tercero, el fino anillo de teflón en su punta abierta para mantener la coaxialidad de los conductores, deberíamos reemplazarlo por un terminador tipo “short” hecho a medida para la sonda (dimensiones y rosca). Esto traería dos ventajas. Una es que el mismo terminador diseñado correctamente sirve como guía para mantener la coaxialidad del sistema. La otra, es que se elimina el anillo de teflón visto como carga, como así el “open” y se reemplaza la carga por un “short”, lo cual es una referencia mucho más precisa.

Igualmente, se concluye que el presente trabajo es un buen avance para demostrar que el método de medición prueba ser útil para caracterizar materiales líquidos donde su preparación en otros métodos convencionales puede ser engorrosa y en algunos casos poco realizables.

# 6. REFERENCIAS

[1] AN 5989-2589EN Agilent Technologies
[2] AN 5991-2171EN Agilent Technologies
[3] Permittivity and Measurements. Komarov, Wang, Tang.
[4] Agilent 85070D, Dielectric Probe Kit Product Overview

IEEE Transactions on instrumentation and measurement, VOL 46 NO 5 October 1997

UTN – FRBA – ME2 Febrero, 2016

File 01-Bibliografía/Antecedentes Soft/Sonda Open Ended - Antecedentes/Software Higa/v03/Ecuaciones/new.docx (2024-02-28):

Γ_(in) =s_11

Z_e =Z_o ((1+Γ_(in) ))/((1-Γ_(in) ))

Z_e =Z_o ([Z_L +jZ_o tan(βx)])/([Z_o +Z_L jtan(βx)])=(Z_o)/(jtan(βx))

Z_o ((1+Γ_(in) ))/((1-Γ_(in) ))=(Z_o)/(jtan(βx))

(1+Γ_(in))/(1-Γ_(in))=1/(jtan(βx))

jtan(βx)=(1-Γ_(in))/(1+Γ_(in))

tan(βx)=-j(1-Γ_(in))/(1+Γ_(in))

βx=tan^(-1) (-j(1-Γ_(in))/(1+Γ_(in)))

β=1/xtan^(-1) (-j(1-Γ_(in))/(1+Γ_(in)))

(2π)/λ=1/xtan^(-1) (-j(1-Γ_(in))/(1+Γ_(in)))

1/λ=1/(2πx)tan^(-1) (-j(1-Γ_(in))/(1+Γ_(in)))

(f√ε)/c=1/(2πx)tan^(-1) (-j(1-Γ_(in))/(1+Γ_(in)))

ε=[c/(2πxf)tan^(-1) (-j(1-Γ_(in))/(1+Γ_(in)))]^2

ε=A^2

A=Btan^(-1) (C)

B=c/(2πxf)

C=-j(1-Γ_(in))/(1+Γ_(in))

jtan(βx)=(1-Γ_(in))/(1+Γ_(in))

jtan((2πxf√ε)/c)-(1-Γ_(in))/(1+Γ_(in))=0

A-B=0

A=jtan((2πxf√ε)/c)

B=(1-Γ_(in))/(1+Γ_(in))

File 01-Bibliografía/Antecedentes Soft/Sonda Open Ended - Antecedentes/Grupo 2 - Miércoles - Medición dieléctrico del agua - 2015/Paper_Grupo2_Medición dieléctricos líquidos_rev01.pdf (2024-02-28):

UTN.BA – Medidas electrónicas II – Año 2015 | 1

Abstract—La caracterización de las propiedades dieléctricas de los materiales a frecuencia de radio ha ganado cada vez más importancia, en especial en los campos de investigación en circuitos de microondas, ya que permite obtener resultados del comportamiento eléctrico y/o magnético del material.

Index Terms— Constante dielectrica, Permititividad, Parametros S, Scattering.

I. INTRODUCCION
a medición de las propiedades dieléctricas implica caracterizaciones de la relación entre la permitividad relativa (εr) y la permeabilidad relativa (μr) de los materiales. La permitividad dieléctrica se compone de una parte real y una parte imaginaria:
- La parte real, se conoce como constante dieléctrica. Es una medida de la cantidad de energía almacenada en el material, producto de un campo eléctrico externo.
- La parte imaginaria, se conoce como factor de pérdida. Es una medida de la cantidad de energía disipada.
El término tang(ɣ) representa la relación entre la parte imaginaria y la real, llamada tangente de perdida o factor de disipación[1].

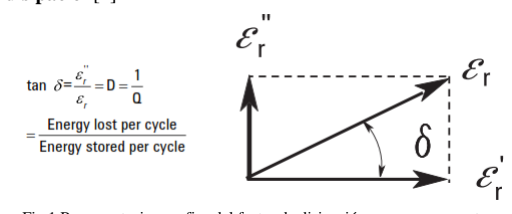
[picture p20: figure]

Fig.1 Representacion grafica del factor de disipación y sus componentes.
La permeabilidad relativa también consta de una parte real, que representa la cantidad de energía almacenada debido a un campo magnético; mientras que la parte imaginaria representa las pérdidas magnéticas del material. La medición de la permeabilidad solo es aplicable a los materiales magnéticos, siendo la mayoría no magnéticos, la permeabilidad es muy cercana a la del espacio libre.

II. DISTINTOS METODOS DE MEDICIÓN Muchos métodos han sido desarrollados, cada uno se limita a frecuencias específicas, materiales y aplicaciones. El avance de la tecnología ha permitido utilizar programas e instrumentos que facilitan la obtención de los parámetros de transmisión y reflexión. Entre los procedimientos destacados se pueden encontrar: Método de la línea de transmisión/reflexión, método espacio libre, método por resonancia y método por sonda coaxial, siendo este último el utilizado en este proyecto[2].

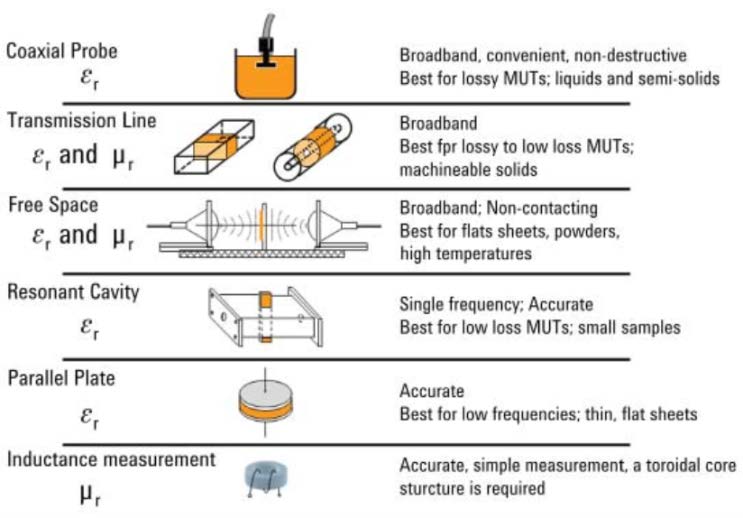
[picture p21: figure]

Fig.2 Distintos métodos y sus aplicaciones.
III. METODO POR SONDA COAXIAL Ventajas:
- No requiere mecanizado del material bajo ensayo.
- Luego de la calibración, la repetibilidad del ensayo es elevada.
- La medición puede realizarse en un ambiente de temperatura controlada.
Desventajas:
- Solo puede medir el parámetro de reflexión.
- Se ve afectada por gaps de aire entre la sonda y la muestra.

El método consiste en la utilización de un cable coaxial como material por donde propagar la señal y se realiza utilizando tres herramientas:

# Medición de permitividad eléctrica en líquidos con parámetros S

Ariel Das, Deborah Higa, LucianoCismondi, Pablo Grass, Alumnos UTN.BA arieldas@hotmail.com, debihiga@gmail.com, cismondil@gmail.com, grass.pablo@gmail.com

L

- Vector Network Analyzer (VNA): Realiza la medición del parámetro S11 en función de las frecuencias programadas. Consiste en un generador de señal que exita a una determinada frecuencia al dispositivo bajo prueba (MUT, Material Under Test). El Receptor sintonizado a dicha frecuencia, detecta las señales transmitida y reflejada del MUT y el Display muestra el módulo y la fase de la transmisión y reflexión en función de la frecuencia.

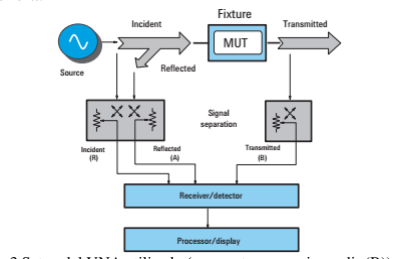
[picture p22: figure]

Fig.3 Setup del VNA utilizado (en nuestro caso, sin medir (B)).
De esta manera, permite la medición de los parámetros S, siendo el de interés el parámetro S11, el coeficiente de reflexión de la tensión del puerto de entrada.
- Sonda: cable coaxial abierto (“open-ended”) utilizado como transductor para la medición de la permitividad de un material. Se llena el coaxial con el material líquido, provocando un cambio en los campos eléctricos y magnéticos en el coaxial y permitiendo así relacionar la medición del parámetro S11 con la permitividad del material.
- Software: convierte el parámetro S11 obtenido de la medición en la permitividad. Se realiza a través de algoritmos iterativos.

IV. CONSTRUCCIÓN DE LA SONDA
La mecanización de la sonda se realizó teniendo en cuenta la impedancia característica del sistema a 50Ω con un dieléctrico de aire. Además era primordial prestar atención a la necesidad de poder introducir un líquido dentro de la sonda para que actúe como dieléctrico.
Contruimos una sonda de cobre de un diámetro exterior suficiente para que pueda alojar un conector tipo N en una de sus extremos. Ademas, la varilla de cobre más fina que conseguimos era de 8mm de diámetro, asi que nos fijaba la dimensión “d”, lo que nos deja calcular D:

# ZZZZ = 1 2. ππ. σσ . ln

DD
dd

= ηη0

# 2. ππ . ln

DD
dd

# ZZZZ = 120. ππΩ 2. ππ . ln

18,4
8 = 50Ω

Otro tema a resolver es que dadas las dimensiones del conector tipo N y su dielectrico adaptamos el extremo de nuestro conducto central al pin central del conector, siempre manteniendo la relación de diámetros para mantener la impedancia caracteristica.


Fig.4 Plano de la sonda construida [mm].

V. MÉTODO DE CONVERSIÓN

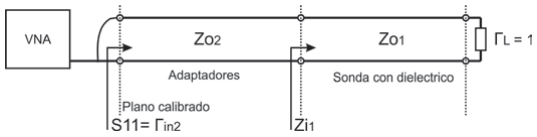
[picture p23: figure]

Fig.5 Setup de medición utilizado.
El plano que figura como “calibrado”, es el punto donde se realizo la calibración del VNA con el método OSM. Partiendo de la medición del S11:

# ΓΓiiii2 = ss11 ZZ 2 = ZZZZ2

# 1 + ΓΓiiii2 1 − ΓΓiiii2 ZZ 1 = jjZZZZ2

2

# .tttt(ββ2ll2) − ZZ 2ZZZZ2 jjZZ 2.tttt(ββ2ll2) − ZZZZ2

ZZ 1 =

1

# 2ππ μμ0 εε0εε∗ . ll ⁡

bb
aa
jj

# 2ππ√εε∗. ff. ll1

cc

Donde igualando las dos ultimas ecuaciones, podemos resolver iterativamente el εε∗ (ya que el mismo esta dentro de

una función tangente).

VI. RESOLUCION DE LAS ECUACIONES POR SOFTWARE
Nuestra ecuación a resolver es:
0 =

1

# 2ππ μμ0 εε0εε∗ . ll ⁡

bb
aa
jj

# 2ππ√εε∗. ff. ll1

cc

− ZZ 1

Para resolver la ecuación no lineal de incógnita compleja se utilizó la función fsolve de la librería scipy de Python. También podría usarse la función con el mismo nombre pero de Matlab. Ambas buscan las raíces de una ecuación pero mediante distintos algoritmos: en el caso de Python, utiliza MINPACK’shybrdyhybrj; y en el caso de Matlab, se puede elegir entre tres opciones: 'trust-region-

## dogleg','trust-region-reflective' y

'levenberg-marquardt'.

fsolve recibe como parámetros obligatorios la ecuación a resolver y un valor estimado de las raíces. Este último parámetro es importante por dos razones:
1) Desde este punto empieza a iterar hasta llegar al resultado, sino a determinada cantidad de iteraciones la función devuelve el último resultado al que llegó e indica que no logró converger.
2) Nuestra ecuación tiene infinitas soluciones. Esto se puede observar desde una perspectiva de una variable donde las soluciones son las intersecciones gráficas entre una tangente y una hipérbola.

Por lo tanto, es importante conocer los valores teóricos y proporcionárselos a la función para que no diverja y para que no caiga en soluciones locales no deseadas. Para ello, recurrimos al modelo deDebye:

# εε∗ = εε∞ +

# εεSS − εε∞ 1 + jjjjjj

εε∞: pppppppp pp aa aa aa ff ff .
εεSS: pppppppp pp aa aa aa ll ff ff 0 ( átt ). :tt dd ó .

Tanto εεSS como son inversamente proporcionales a la

temperatura. Basándonos en [4] obtuvimos los valores empíricos para cada frecuencia y temperatura del agua destilada, que se detallaran en la parte de mediciones.

| VII. MEDICIONES
A. Agua destilada

Fig.6 Comparacion tangente de perdida teorica y medida @26º.

Fig.7 Comparacion tangente de perdida teorica y medida @40º.

Fig.8 Comparacion tangente de perdida teorica y medida @54º.

Fig.9 Comparacion tangente de perdida teorica y medida @60º.

VIII. CONCLUSIÓNES
Comparando las mediciones obtenidas, con los valores teoricos calculados, podemos notar tres tendencias significativas.
La primera es que las mediciones tienen un alto valor de dispersión. Consideramos que es debido al error de método de medición (configuración mecánica de la sonda, VNA, agua utilizada) ya que se puede observar que para todas las mediciones a diferentes temperaturas, la forma de los datos en función de la frecuencia se repite sistematicamente.

La segunda, es que a frecuencias mayores que 1GHz la curva teorica tiende a aumentar, y las mediciones tienen a disminuir. Esto es debido a la frecuencia de corte de la sonda. Si la calculamos, tomando la formula para un cable coaxial:

# ffCC[GGHHHH] = 190,5

# √εε (DD + dd)[ ]

= 190,5
√81(18,4 + 8)[ ]

# = 0.803[GGHHHH]

Podemos ver que el valor teorico es cercano a la frecuencia donde notamos que la curva empieza a decrecer en vez de subir.

La tercera y mas importante, es que a frecuencias comprendidas entre 100MHz y 1GHz y pese a la dispersión, el valor medio de la curva medida, sigue a la curva teorica. Inclusive comparamos el valor medio de la parte real (constante dieléctrica) con valores obtenidos en [5] y resultan
bastante | similares.

Ademas, la sonda en su configuración original, tenía un fino anillo de teflón en su punta abierta para mantener la coaxialidad de los conductores. Esto trae aparejado dos problemas. Uno, que en los cálculos teoricos tomabamos como carga de la sonda una carga abierta, sin considerar los problemas de borde para el campo electromagnetico. El segundo es que en realidad, dicho anillo de teflón debería considerarse como carga de la sonda, siendo este un capacitor

-0.5

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
100 | 1000

Tangente de pérdida

Frecuencia [MHZ]

Agua 26°C (Prom:10,76)

Teórico Agua 26°C

-0.5

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
100 | 1000

Tangente de pérdida

Frecuencia [HZ]

Agua 40°C (Prom:7,36)

Teórico Agua 40°C

-0.5

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
100 | 1000

Tangente de pérdida

Frecuencia [HZ]

Agua 54°C (Prom:5,34)

Teórico Agua 54°C

-0.5

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
100 | 1000

Tangente de pérdida

Frecuencia [HZ]

Agua 60°C (Prom:6,35)

Teórico Agua 60°C coaxial a calcular y contemplar en los cálculos.

Igualmente, concluimos que el presente trabajo es un buen avance para demostrar que el método de medicion prueba ser útil para caracterizar materiales líquidos donde su preparación en otros métodos convencionales puede ser engorrosa y en algunos casos poco realizables.

IX. TRABAJOS FUTUROS
Con respecto a la sonda, fue un buen primer prototipo, pero tenemos que rediseñarla.
Primero, que la misma tenga un conector tipo N macho, tal cual tienen los patrones OSM que utilizamos y no agregar elementos a la incertidumbre de medición, como ser adaptadores.
Segundo, hay que rediseñar las dimesiones “D y d” de acuerdo a una frecuencia de corte de 3 o 3.5GHz con un εε = 81 (agua) y que mantenga una ZZ = 50Ω para el aire.

Tercero, el fino anillo de teflón en su punta abierta para mantener la coaxialidad de los conductores, deberíamos reemplazarlo por un terminador tipo “short” hecho a medida para la sonda (dimensiones y rosca). Esto traería dos ventajas. Una es que el mismo terminador diseñado correctamente sirve como guía para mantener la coaxialidad del sistema. La otra, es que se elimina el anillo de teflón visto como carga, como asi el “open” y se reemplaza la carga por un “short”, lo cual es una referencia mucho mas precisa.

X. REFERENCIAS
[1] AN 5989-2589EN Agilent Technologies
[2] AN 5991-2171EN Agilent Technologies
[3] Permittivity and Measurements. Komarov, Wang, Tang.
[4] Agilent 85070D, Dielectric Probe Kit Product Overview
[5] IEEE Transactions on instrumentation and measurement, VOL 46 NO 5 October 1997

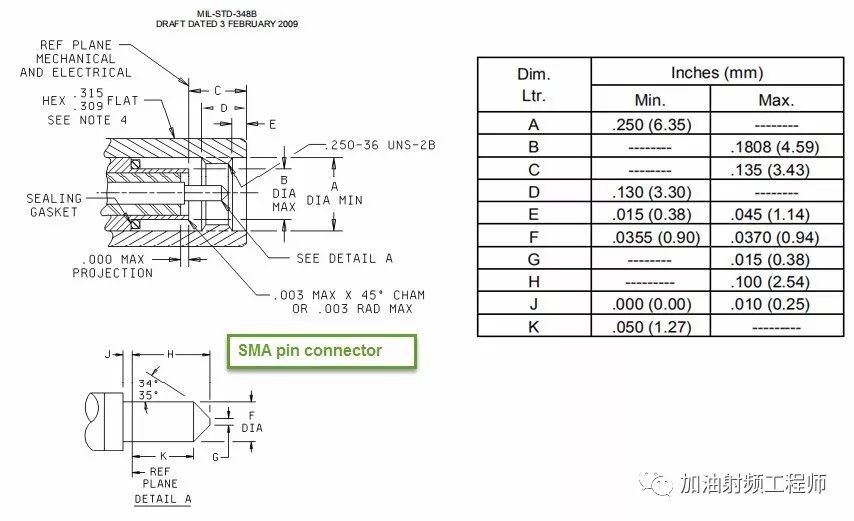
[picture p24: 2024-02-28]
03-Diseños/SMA/MBXY-CR-46d4bd047ff558f94ddf696ebdcfd4d1.png

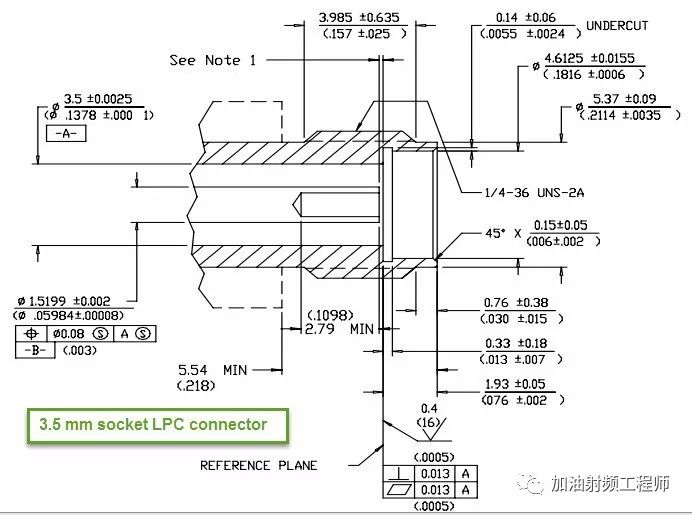
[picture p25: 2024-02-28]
03-Diseños/SMA/MBXY-CR-0249249f3ff1b1c7a5238aef57cc0de9.png

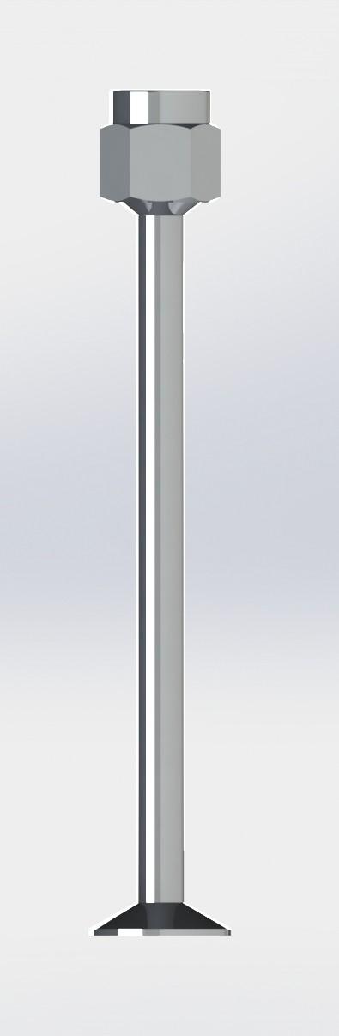
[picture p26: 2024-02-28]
03-Diseños/Imagenes/SONDA_SMA.JPG

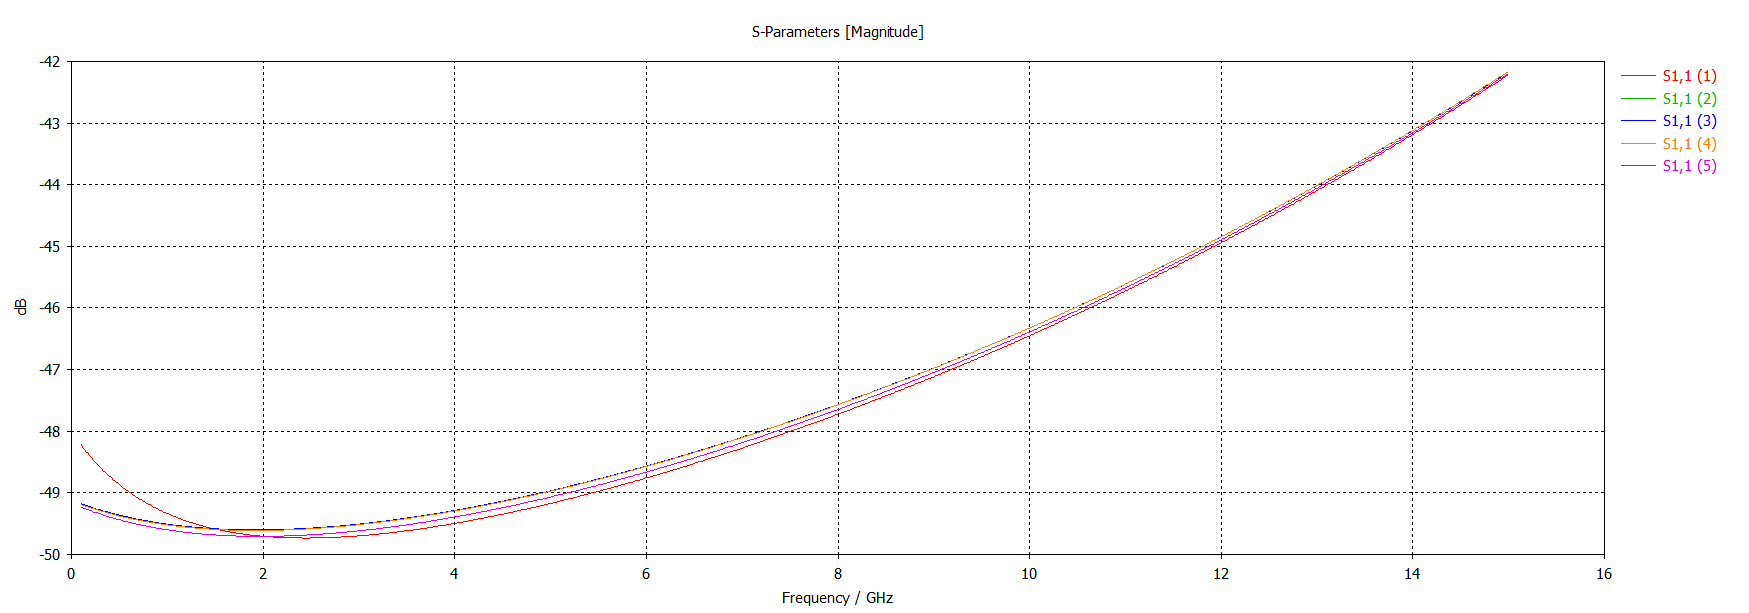
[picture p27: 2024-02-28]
04-CST/Sonda_v2/Temp/clipboard.bmp

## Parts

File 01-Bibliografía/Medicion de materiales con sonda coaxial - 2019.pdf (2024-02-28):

# Informe de proyecto de laboratorio:

# Medici´on de semi-s´olidos con sonda coaxial hasta 18 GHz

# Medidas Electr´onicas II

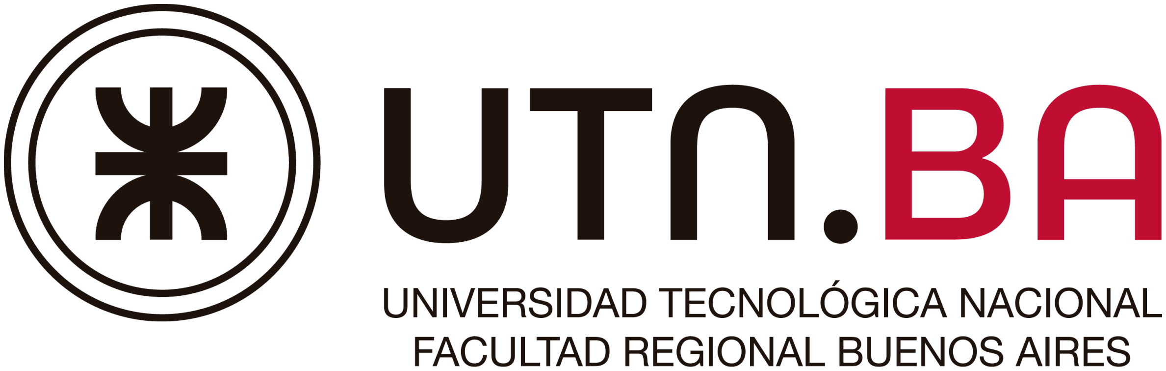
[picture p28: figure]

## Profesor adjunto: Ing. Alejandro Henze Ayudante: Ing. Guillermo Monasterios

Alumnos: Barrios Maximiliano - 149.512-4 Ebrecht Agust´ın - 155.418-2 Fritzler Pablo - 155.413-0 Tucci Federico - 149.827-7

CABA, Argentina, Octubre 2019

## ´Indice

1. Introducci´on | 1
2. Introducci´on del m´etodo | 1
3. Construcci´on de la sonda | 2
3.1. Construcci´on de la primer sonda | | 3
3.2. Construcci´on de la segunda sonda | | 3
4. Software, automatizaci´on y m´etodo detallado | 4
4.1. Automatizaci´on con MatLab | | 4
4.2. Patrones utilizados | | 5
4.2.1. Agua destilada | | 6
4.2.2. Alcohol isoprop´ılico | | 6
5. Corroboraci´on con software y primera medici´on | 7
6. Desarrollo matem´atico | 8
7. Piezas 3D necesarias | 8
8. Mediciones hechas | 9
8.1. Comparaci´on de pieles | | 9
9. Mejoras a futuro | 10
10.Conclusiones | 10
11.Bibliograf´ıa | 11

## 1. Introducci´on

El estudio de las propiedades electromagn´eticas de los materiales org´anicos es de amplio inter´es para diversas disciplinas de la salud y la biolog´ıa. El tejido humano es un material heterog´eneo que contiene agua, mol´eculas org´anicas disueltas, macromol´eculas, iones y materia insoluble. Todos estos elementos est´an organizados en estructuras celulares y subcelulares formando unidades macrosc´opicas y tejidos duros y blandos. La presencia de iones juega un papel importante en la interacci´on con un campo el´ectrico, proporcionando medios para la conducci´on i´onica y efectos de polarizaci´on. La respuesta de toda materia a una onda electromagn´etica viene descrita por las ecuaciones de Maxwell. Seg´un ´estas, aquella depende de los par´ametros intr´ınsecos de la materia: la permeabilidad µ, la permitividad ε y la conductividad σ. La mayor parte de la materia biol´ogica tiene una permeabilidad magn´etica similar a la del vac´ıo µ0, por lo que el an´alisis de su respuesta cuando se excita con frecuencias distintas se centra en la conductividad y en la permitividad relativa a la del vac´ıo. Estos par´ametros constitutivos de la materia proporcionan, por un lado, la capacidad para permitir el movimiento de portadores de carga y, por otro, una medida de su polarizabilidad. En este proyecto se replicaron resultados de mediciones de permitividad relativa para distintos tipos de materiales en un rango de hasta 10GHz, utilizando un VNA (y su respectiva calibraci´on), realizando la medici´on a un puerto (Par´ametro S11) a trav´es de una sonda coaxial.

## 2. Introducci´on del m´etodo

El m´etodo en general consiste en apoyar superficialmente una sonda sobre un tejido, y en base a ciertos c´alculos matem´aticos poder decir la permitividad el´ectrica que tiene, de manera no invasiva y sin procesos traum´aticos, tambi´en de manera muy r´apida.

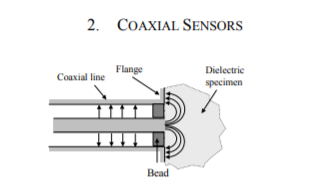
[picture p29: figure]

Figura 1: Principio de funcionamiento de una sonda coaxial.

Para lograr esto se tuvieron que tener que llevar a cabo determinados procesos:

Construcci´on de una sonda

Garantizar el buen funcionamiento de la sonda

Creaci´on de un m´etodo de calibraci´on

Conseguir datos sobre permitividades el´ectricas de ciertos tejidos para poder corroborar las mediciones hechas.

Creaci´on de un software que nos permita automatizar el proceso con el VNA.

Medici´on y comparaci´on de distintos tipos de pieles.

## 3. Construcci´on de la sonda

El primer paso consisti´o en la selecci´on y acondicionamiento de tres cables coaxiales semir´ıgidos, para convertirlos en sondas de medici´on, los cuales fueron provistos por la c´atedra y otros conseguidos en el mercado. El acondicionamiento consisti´o en el cortado, emprolijamiento de la misma y el agregado de una arandela conductora, la cual deb´ıa estar mec´anicamente en el mismo plano que el perteneciente al corte transversal de la sonda.

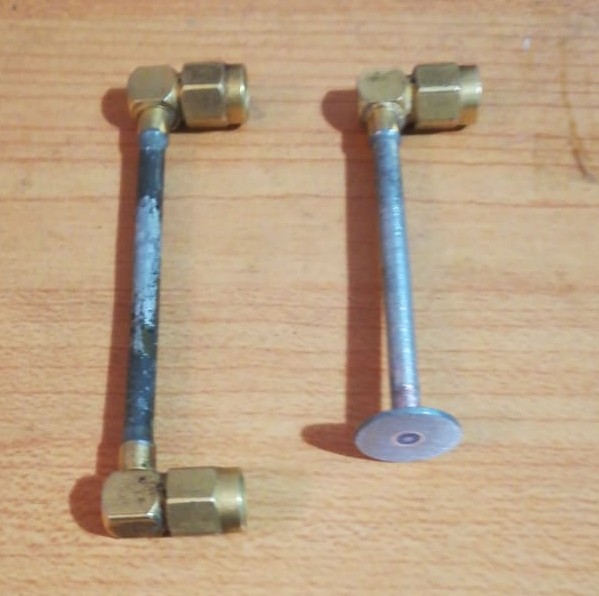
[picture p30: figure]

Figura 2: Sonda antes y despu´es del proceso.

Esta arandela debe captar las ondas electromagn´eticas que se formen en la terminaci´on de la sonda y para ´ verificar su correcto funcionamiento, se realizaron mediciones de corto circuito y circuito abierto, analizando con el VNA para todas las frecuencias de inter´es, que el m´odulo se mantenga constante con valor 1 y la fase sea la correspondiente al CC o CA.

### 3.1. Construcci´on de la primer sonda

La primer sonda se construy´o en base al soldado de la arandela a la sonda, el diagrama de Smith deber´ıa mostrar a circuito abierto un m´odulo de 1 para todas las frecuencias de inter´es, pero revelaron que no se cumpl´ıa:

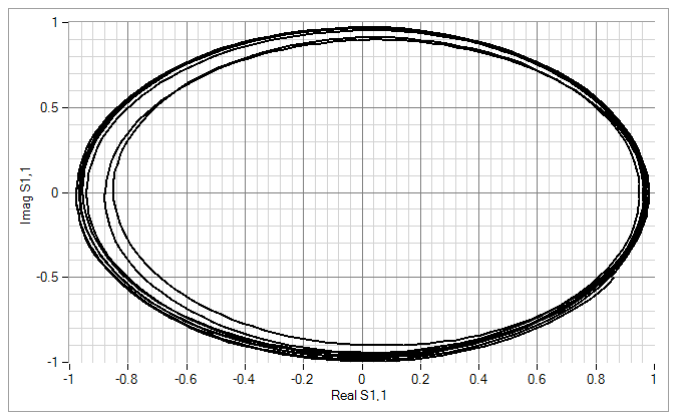
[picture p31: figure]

Figura 3: Diagrama de Smith de VNA tools de la primer sonda.

### 3.2. Construcci´on de la segunda sonda

La segunda sonda se construy´o en base al a˜nadido de la arandela a presi´on con ayuda de pegamento. Las pruebas con el diagrama de Smith del VNA mostraron que fue mejor este m´etodo:

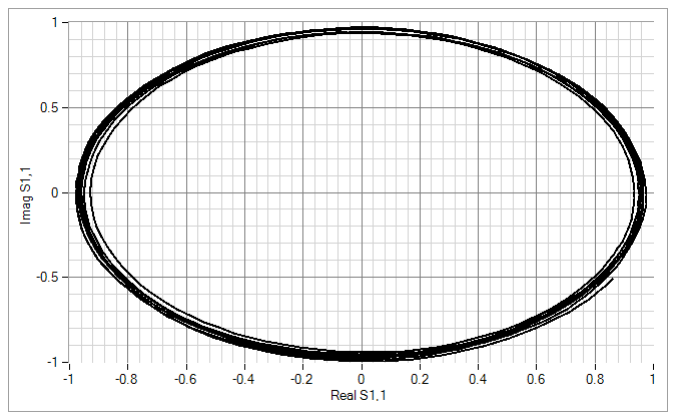
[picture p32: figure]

Figura 4: Diagrama de Smith de VNA tools de nuestra segunda sonda.

## 4. Software, automatizaci´on y m´etodo detallado

### 4.1. Automatizaci´on con MatLab

El segundo paso consisti´o en la automatizaci´on del VNA y el desarrollo de un software en MATLAB que permitiera adquirir las muestras de manera repetitiva y ordenada, as´ı como tambi´en podr´ıamos manejar el VNA con una interfaz gr´afica, realizar la graficaci´on de las se˜nales, almacenamiento de datos, etc.
El primer paso en este proceso fue la creaci´on de los drivers, que constaron en una funci´on de inicializaci´on, una funci´on de desconexi´on y cierre, una funci´on para hacer una medici´on y obtener los datos de la medici´on. La bibliograf´ıa m´as ´util para crear los drivers que comunican a MatLab con el VNA fue el mismo manual de Keysight.

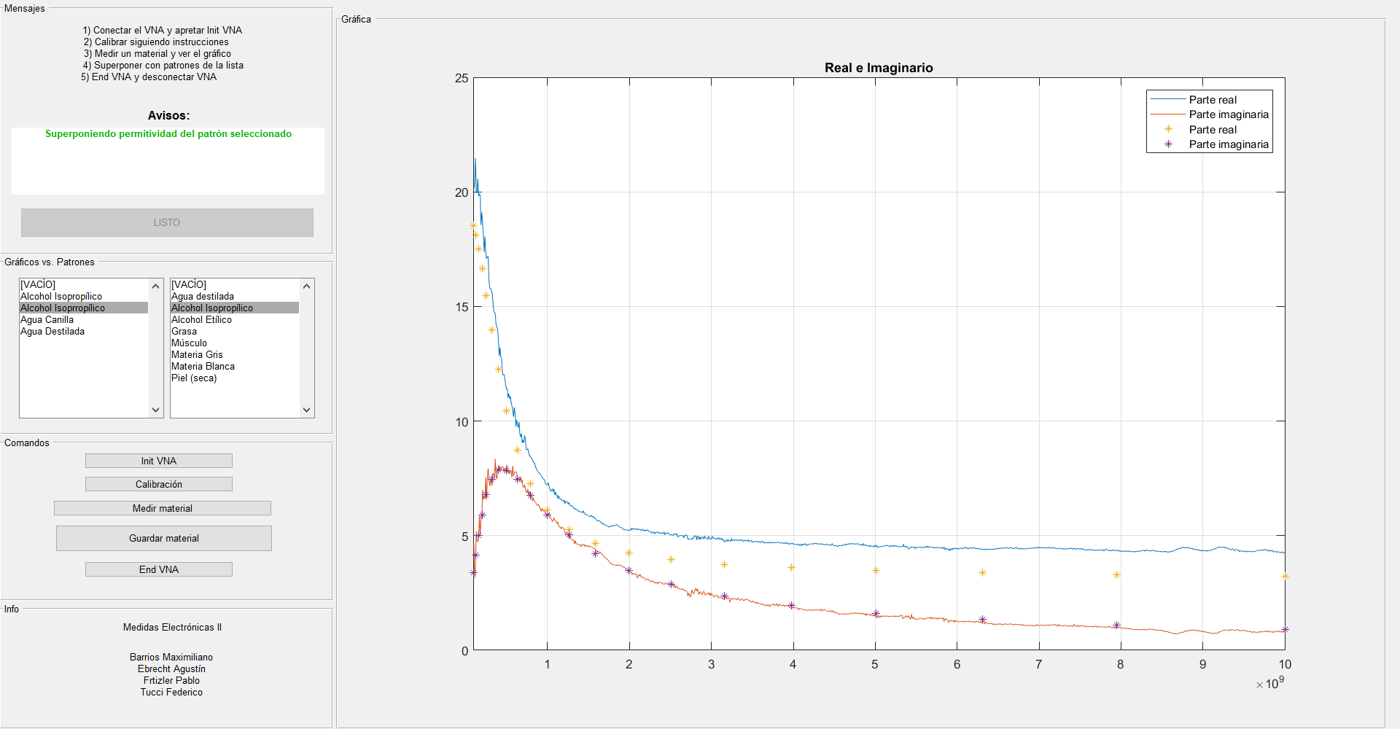
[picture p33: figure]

Figura 5: Programa creado para nuestro prop´osito.

En t´erminos generales, el software desarrollado gu´ıa al usuario en la calibraci´on del equipo, informando los materiales que debe ir colocando para la misma. Posteriormente se puede comenzar con la caracterizaci´on de cualquier material/tejido que se encuentre en contacto superficial con la sonda coaxial.

Deben tenerse en cuenta algunas consideraciones :

La sonda puede oxidarse en caso de estar en contacto con materiales h´umedos, es recomendable realizar una limpieza de la misma luego de cada medici´on y preferentemente con el mismo l´ıquido que se quiera medir posteriormente.

El contacto con la sonda debe ser superficial pero con cierta presi´on, para evitar que las l´ıneas de campo se escapen de la arandela conductora y sean captadas para una correcta medici´on de la onda reflejada.

Los barridos realizados por el VNA disponible en UTN FRBA al d´ıa de la fecha, nos permitieron realizar las mediciones desde los 100 MHz hasta los 10 GHz, sin embargo la sonda podr´ıa utilizarse en principio, hasta los 40 GHz.

Es importante considerar la profundidad de penetraci´on en el caso de l´ıquidos, ya que la onda incidente y reflejadas pueden verse afectadas por el rebote de un contenedor pl´astico/met´alico que puedan modificar el par´ametro S medido.

Las ondas son no ionizantes por lo cual no supone bajo ning´un punto de vista un inconveniente para la interacci´on con tejidos in vivo.

Tambi´en es importante destacar que el software cuenta con una base de datos, en la cual se almacenan curvas patrones (IFAC), las cuales pueden verse en simult´aneo con las mediciones que se est´en tomando para realizar comparaciones entre ambas. La precisi´on de la medici´on no se ve afectada frente a la reducci´on de la cantidad de puntos tomados ( en el eje frecuencial ) por lo que no es necesario despreciar la conductividad para disminuir el tiempo de procesamiento de las muestras, llegando incluso a realizar las mediciones en 30 seg. obteniendo posteriormente el gr´afico en pantalla en otros 30 seg. Tambi´en pueden exportarse las mediciones tomadas en formato s1p, un est´andar en archivos de medici´on de par´ametros S para luego realizar un an´alisis e interpretaci´on de los datos en cualquier software que se desee ( adem´as de VNA Tools ). Es posible tambi´en con algunos ajustes exportarlo a otros formatos, aunque no est´e contemplado en el que aqu´ı se detalla.

### 4.2. Patrones utilizados

Una vez que fue posible comunicarse con el VNA, chequeando el correcto funcionamiento del mismo, se debi´o definir una calibraci´on para luego comenzar con las mediciones. La calibraci´on consiste en un m´etodo similar a OSM, con la diferencia de que en el caso de estudio no cont´abamos con el patr´on de match (impedancia adaptada), por lo que se utilizaron como patrones : cortocircuito, circuito abierto, alcohol et´ılico y agua destilada. Se optaron por estos 4 patrones ya que los primeros dos forman parte de un est´andar, mientras que los otros 2 elementos, son conocidos por diversos estudios en frecuencias de microondas y sus permitividades el´ectricas se encuentran caracterizadas en diferentes curvas.

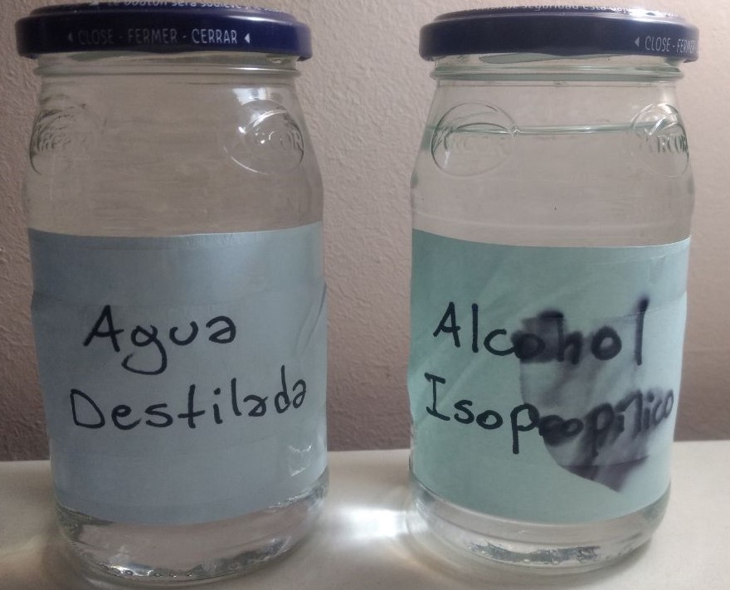
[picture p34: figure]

Figura 6: Frascos en los que se inserta la sonda durante la calibraci´on.

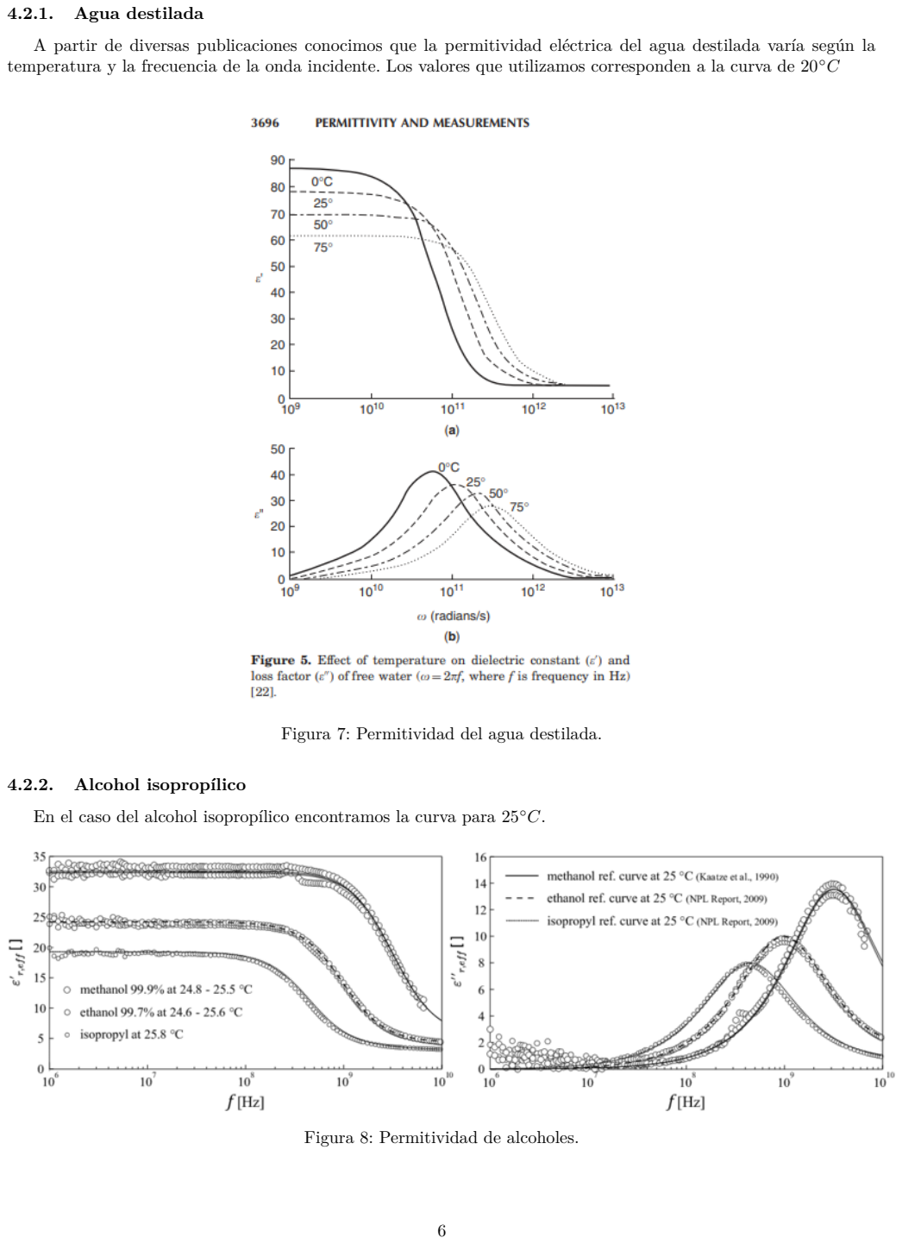
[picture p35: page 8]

### 4.2.1. Agua destilada

A partir de diversas publicaciones conocimos que la permitividad el´ectrica del agua destilada var´ıa seg´un la temperatura y la frecuencia de la onda incidente. Los valores que utilizamos corresponden a la curva de 20◦C

Figura 7: Permitividad del agua destilada.

### 4.2.2. Alcohol isoprop´ılico

En el caso del alcohol isoprop´ılico encontramos la curva para 25◦C.

Figura 8: Permitividad de alcoholes.

## 5. Corroboraci´on con software y primera medici´on

Al llegar a este punto fue fundamental comparar una medici´on de algo conocido junto con su curva te´orica, para esto elegimos medir alcohol isoprop´ılico, dado que era el ´ultimo patr´on utilizado, y para medir no hac´ıa falta retirar la sonda de su ´ultima medici´on.
Los resultados fueron muy satisfactorios:


Figura 9: Alcohol isoprop´ılico medido y comparado con la curva te´orica.

Como se ve en la figura anterior, la curva te´orica se muestra en amarillo y violeta y con el s´ımbolo *. La curva medida se muestra en rojo y azul, la azul comparado con la te´orica tiene un error muy bajo y la roja pr´acticamente es una copia de la te´orica.
El siguiente paso fue medir algo conocido, conociendo la curva te´orica del tejido muscular elegimos medir carne vacuna con resultados tambi´en muy satisfactorios:


Figura 10: Comparaci´on de carne vacuna con tejido muscular.

## 6. Desarrollo matem´atico

Para llegar a la obtenci´on de estas curvas, fue necesario comprender el c´alculo de la permitividad el´ectrica de un material, el cual se compone por una parte real e imaginaria y cuyos valores se pueden obtener a partir de la f´ormula de Debye. La misma consigue caracterizar el εr a partir de la conductancia y la capacidad de la sonda y el material medido, las cuales se estiman a partir de la conversi´on de par´ametros S a par´ametros admitancia, haciendo uso de un modelo de par´ametros concentrados de antena.


Figura 11: Sonda coaxial y modelo de la misma con un tejido.

El proceso matem´atico est´a descripto en el informe “Medici´on de permitividad el´ectricas en l´ıquidos con par´ametros S, Ing. Ariel Das, Ing. Deborah Higa, Ing. Luciano Cismondi, Pablo Grass, Universidad Tecnol´ogica Nacional, Facultad Regional Buenos Aires, Departamento de Ingenier´ıa Electr´onica, 2015”

## 7. Piezas 3D necesarias

Se cre´o un soporte para facilitar la inmovilidad de los cables del VNA y garantizar una mayor calidad de mediciones:


Figura 12: Sonda coaxial en su soporte.

## 8. Mediciones hechas


### 8.1. Comparaci´on de pieles

Figura 13: Diferencia entre las medias de pieles secas y h´umedas.

Estos valores fueron obtenidos de la p´agina italiana http://niremf.ifac.cnr.it/tissprop/htmlclie/htmlclie.php. Los valores que obtuvimos de brazos de varias personas son diferentes a estas curvas te´oricas:

Figura 14: Superposici´on de 11 mediciones diferentes de brazos.

Es importante tener en cuenta que en la “Figura 13” la parte imaginaria se muestra como positiva para facilitar la visualizaci´on en el mismo gr´afico que la parte real. En cambio en la “Figura 14” no est´a este cambio de signo. Se aprecia que en las curvas te´oricas existe una pendiente, negativa en el caso de la parte real, y positiva para la parte imaginaria. En el caso de las mediciones hechas, en promedio, no hay ning´un tipo de pendiente en la parte real, y no tan pronunciada en la parte imaginaria.

## 9. Mejoras a futuro

Como posibles mejoras estamos seguros que el ambiente de medici´on tiene un gran impacto sobre la calidad de la calibraci´on, y por ende, en la calidad de la medici´on que se toma. Las mediciones de piel observadas anteriormente fueron tomadas en una exposici´on de “Feria de proyectos”, con ubicaci´on en la sede Campus, con lo cual la calibraci´on que se hizo en el lugar influy´o mucho en las mediciones tomadas. Conclu´ımos de esto que es fundamental estar en un ambiente controlado y libre de perturbaciones tanto mec´anicas como clim´aticas al momento de calibrar y tomar mediciones.

Creemos tambi´en que hace falta el desarrollo de un m´etodo sistem´atico de medici´on de las pieles, dado que si bien medimos antebrazos, el lugar espec´ıfico siempre vari´o desde la flexura del codo hasta casi la mu˜neca, en la parte anterior tanto como posterior del antebrazo. No conocemos con precisi´on c´omo fueron hechas las mediciones que tomamos como “valores te´oricos” y entendemos que la humedad de la piel, as´ı como otros factores que tambi´en aportan a la permitividad, var´ıan seg´un la zona.

## 10. Conclusiones

Se pudieron obtener mediciones cuya repetibilidad y repetitividad eran representativas tanto para la materia como para un proyecto de investigaci´on. El aprendizaje logrado gracias al proyecto fue motivado tambi´en en parte por la potencialidad de que a futuro, el mismo pueda detectar anomal´ıas como tumores en tejidos de manera no invasiva. Los conocimientos adquiridos se debieron tanto a la parte te´orica pero m´as a´un por poner en pr´actica los conceptos vistos a lo largo de la materia. Esperamos de esta forma, dejar una base para nuevos proyectos o incluso la continuaci´on/extensi´on del mismo.

## 11. Bibliograf´ıa

[1] AN 5989-2589EN Basics of Measuring the Dielectric Properties of Materials, Keysight Technologies, application note.
[2] 5991-2171EN Measuring Dielectric Properties Using Keysight’s Materials Measurement Solutions, Keysight Technologies, application note.
[3] Evaluation of a Reflection Method on an Open-Ended Coaxial Line and its Use in Dielectric Measurements, Prof. Ing. Jan Vrba, CSc., Doc. Ing. Karel Novotn´y, CSc, Czech Technical University in Prague, Faculty of Electrical Engineering, Technick´a 2, 2006.
[4] Medici´on de permitividad el´ectrica en l´ıquidos con par´ametros S, Ing. Ariel Das, Ing. Deborah Higa, Ing. Luciano Cismondi, Pablo Grass, Universidad Tecnol´ogica Nacional, Facultad Regional Buenos Aires, Departamento de Ingenier´ıa Electr´onica, 2015.
[5] http://niremf.ifac.cnr.it/tissprop/htmlclie/htmlclie.php, Institute for Applied Physics ”Nello Carrara”, Florence, Italy, 2012.
[6] Tables of the Complex Permittivity of Dielectric Reference Liquids at Frequencies up to 5 GHz, A.P. Gregory, R.N. Clarke, 2012.
[7] Programaci´on en Matlab del algoritmo de calibraci´on del modelo capacitivo para sondas coaxiales Mar´ıa Garc´ıa Duarte, Escuela T´ecnica Superior de Ingenier´ıa de Telecomunicaci´on, Universidad Polit´ecnica de Cartagena 2017.
[8] Permittivity and measurements, V. Komarov, S. Wang, J. Tang, Washington State University, 2005.
[9] Permittivity measurements using coaxial probes, A Degree Thesis Submitted to the Faculty of the Escola T`ecnica d’Enginyeria de Telecomunicaci´o de Barcelona Universitat Polit`ecnica de Catalunya by Bartomeu Oliver Riera,
B. Riera, May 2016.
[10] Artificial Human Phantoms: Human proxy in testing microwave apparatus that have electromagnetic interaction with the human body, A. T. Mobashsher, A. M. Abbosh, School of ITEE, The University of Queensland St. Lucia, Brisbane QLD 4072, Australia, 2015.
[11] NIST Technical Note 1554, Characterization of Tissue-Equivalent Materials for High-Frequency Applications (200 MHz to 20 GHz), Jannes Baker-Jarvis, Sung Kim, Luke E. Schallinger, Justin Johnson, Brad Givot, 2010.

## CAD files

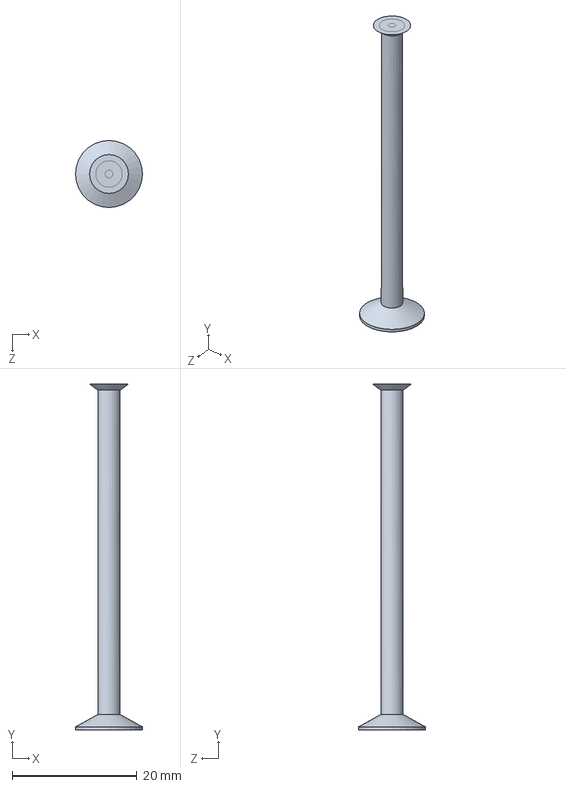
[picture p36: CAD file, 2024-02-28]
03-Diseños/Sonda/Sonda_v1.SLDPRT
10.8 x 55.5 x 10.8 mm

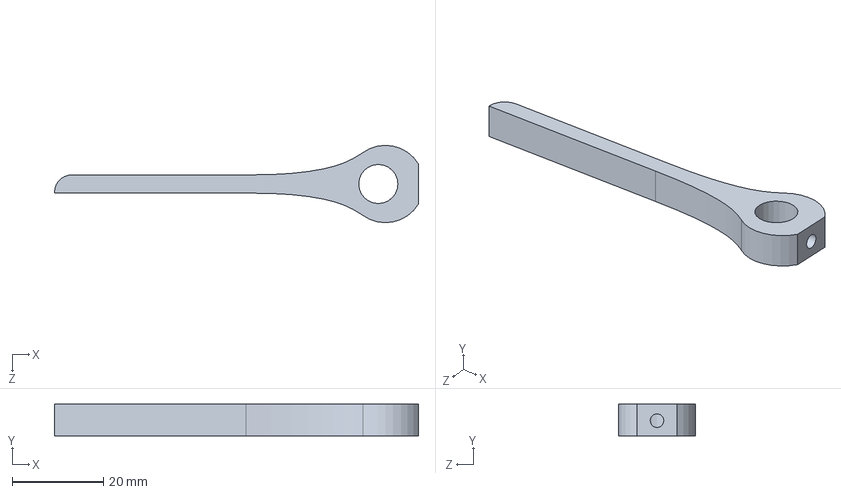
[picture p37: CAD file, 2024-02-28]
03-Diseños/Soportes_onda/Part1.SLDPRT
80.0 x 7.00 x 17.0 mm

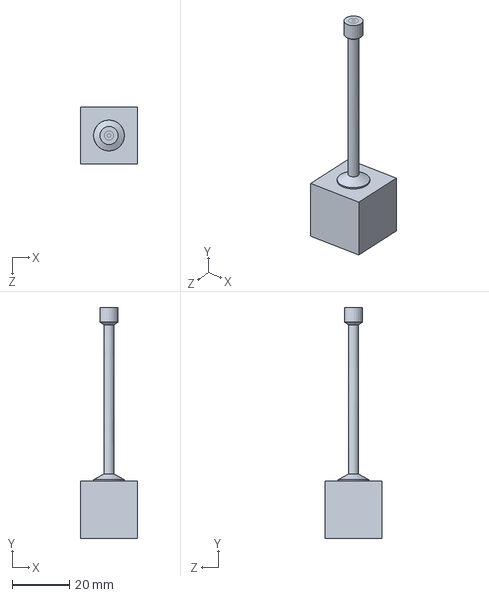
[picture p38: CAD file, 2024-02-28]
04-CST/modelo_sonda/Temp/Node012/Model/3D/Sonda_v2_2.SLDPRT
20.0 x 80.6 x 20.0 mm

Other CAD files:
03-Diseños/SMA/Dielectric.sldprt
04-CST/modelo_sonda/Model/3D/Sonda_v2_1.SLDPRT
04-CST/modelo_sonda/Temp/Node009/Model/3D/Sonda_v2_1.SLDPRT
04-CST/modelo_sonda/Temp/Node010/Model/3D/Sonda_v2_1.SLDPRT
04-CST/modelo_sonda/Temp/Node011/Model/3D/Sonda_v2_1.SLDPRT
04-CST/modelo_sonda/Temp/Node019/Model/3D/Sonda_v2_1.SLDPRT
04-CST/modelo_sonda/Temp/Node020/Model/3D/Sonda_v2_1.SLDPRT
04-CST/modelo_sonda/Temp/Node021/Model/3D/Sonda_v2_1.SLDPRT
03-Diseños/SMA/Gasket.sldprt
03-Diseños/SMA/Key.sldprt
03-Diseños/SMA/Nut.sldprt
03-Diseños/SMA/Pin.sldprt
03-Diseños/SMA/SMA_male_edge_6.5x6.5.SLDASM
03-Diseños/SMA/SMA_male_edge_6.5x6.5.SLDDRW
03-Diseños/SMA/SMA_male_edge_6.5x6.5.STEP
03-Diseños/SMA/SMA_male_edge_6.5x6.5.STL
03-Diseños/SMA/Sleeve.sldprt
03-Diseños/Sonda/Sonda+SMA.STEP
03-Diseños/Sonda/Sonda_v1.SLDDRW
03-Diseños/Sonda/Sonda_v2.SLDPRT
03-Diseños/Sonda/Sonda_v3.SLDPRT
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

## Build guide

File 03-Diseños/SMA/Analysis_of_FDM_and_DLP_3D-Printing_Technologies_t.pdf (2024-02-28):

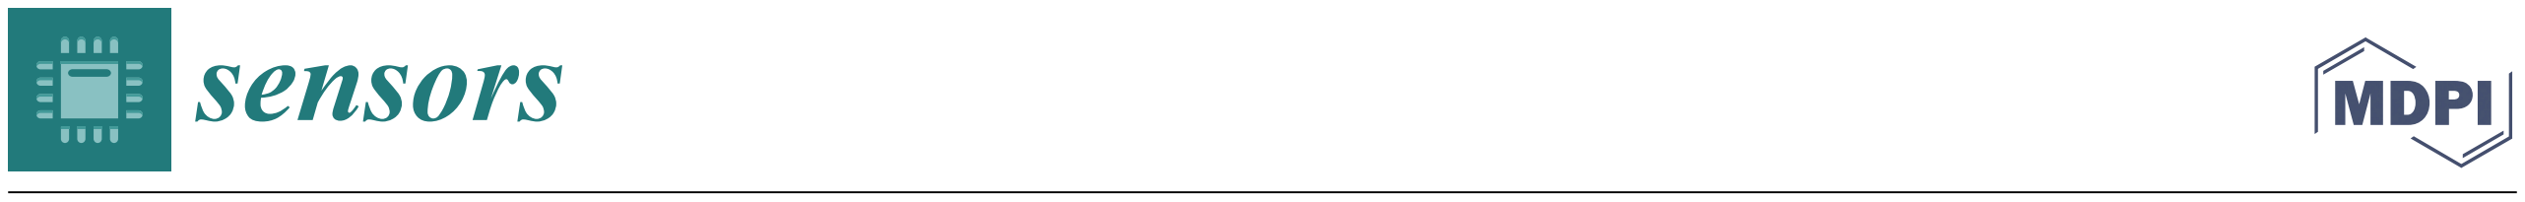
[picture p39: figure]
sensors

Article

# Analysis of FDM and DLP 3D-Printing Technologies to Prototype Electromagnetic Devices for RFID Applications †

Riccardo Colella 1

, Francesco Paolo Chietera 2 and Luca Catarinucci 2,*

(https://www.mdpi.com/1424-8220/21/3/897?type=check_update&version=1)

Citation: Colella, R.; Chietera, F.P.; Catarinucci, L. Analysis of FDM and DLP 3D-Printing Technologies to Prototype Electromagnetic Devices for RFID Applications. Sensors 2021, 21, 897. https://doi.org/10.3390/s21030897 (https://doi.org/10.3390/s21030897)

Academic Editor: Renato Ferrero Received: 7 January 2021
Accepted: 26 January 2021
Published: 29 January 2021

Publisher’s Note: MDPI stays neutral with regard to jurisdictional claims in published maps and institutional affiliations.

Copyright: © 2021 by the authors. Licensee MDPI, Basel, Switzerland. This article is an open access article distributed under the terms and conditions of the Creative Commons Attribution (CC BY) license (https://creativecommons.org/licenses/by/4.0/).

1 | National Research Council of Italy, 73100 Lecce, Italy; riccardo.colella@cnr.it
2 | Innovation Engineering Department, University of Salento, 73100 Lecce, Italy;
| francescopaolo.chietera@unisalento.it
* | Correspondence: luca.catarinucci@unisalento.it
† This paper is an extended verision of our previously published paper “R. Colella, F. P. Chietera and
L. Catarinucci, Digital Light Processing as One of the Promising 3D-Printing Technologies in
| Electromagnetics: Application on RFID”. In Proceedings of the 2020 5th International Conference on Smart
| and Sustainable Technologies (SpliTech), Split, Croatia, 23–26 September 2020, pp. 1–4.

Abstract: In this work, the application in Radiofrequency Identification (RFID) of different additive manufacturing (AM) 3D-printing technologies is discussed. In particular, the well-known Fused Deposition Modeling (FDM) technology is compared with the promising Digital Light Processing (DLP), which is based on the photopolymerization of liquid resins. Based on the research activity of the authors on this topic, a brief introduction to the fundamentals of 3D-printing in electromagnetics as well as to the different applications of both FDM and DLP in realizing Radio Frequency (RF) devices, is firstly given. Then, a comparison of the two technologies is deeply faced. Finally, after evaluated the rugosity of substrates produced with both techniques to verify the potential impact on the design of electromagnetic structures, the two techniques are both exploited for the realization of the dielectric parts of a tunable RFID tag with unconventional shape. It consists of two elements interlinked one each other. The movement between them enables tuning of the resonance frequency as well as the impedance of the antenna. Despite the differences in terms of losses, rugosity, resolution, and dielectric constant, both techniques guaranteed satisfactory values of tag sensitivity, maximum reading range, and tunability. Nevertheless, the careful analysis of the results proposed at the end of the paper suggests how the selection of one technique over the other must be taken considering the specific application constraints.

Keywords: 3D-printing; DLP; FDM; T-Resonator; 3D-printed antennas; UHF; RFID

### 1. Introduction

3D printing by additive manufacturing (AM) is proving to be a promising technology to create high-detailed models wasting less time and spending fewer resources than traditional methods. In the last few years, the advent of more and more accurate and affordable 3D printers has considerably stimulated the electromagnetic community, strongly interested in the realization of microwave components and antennas which take advantage of versatility, cost-effectiveness, and ease of use of these rapid prototyping techniques. Different 3D-printing technologies can be used to produce electromagnetic devices [1–11]. In Farooqui et al. and Fenn et al. [1,2], the Fused Deposition Modelling (FDM) technology has been used to build a cross-polarized (CP) microstrip fed patch antenna in Farooqui et al. [1] and a conformal antenna array in Fenn et al. [2], respectively. In the former case, the conductive parts have been obtained using copper adhesive tape, while in the latter a copper electroplating process has been carried out. In Heirons et al. and Mirmozafari et al. [3,4] a CP patch antenna and a linear array have been described as well, but this time the adopted manufacturing technology has been the Stereo Lithography (SLA) 3D-printing. In these cases, the conductive parts have been realized with inkjet

Sensors 2021, 21, 897. https://doi.org/10.3390/s21030897 | https://www.mdpi.com/journal/sensors

Sensors 2021, 21, 897 | 2 of 13

printing in Heirons et al. [3] and with an electroplating process in Mirmozafari et al. [4]. In Kaddour et al. [5], a Selective Laser Sintering (SLS) process has been used to polymerize polycarbonate (PC) and ABS in other to develop a dual-polarized unidirectional wideband antenna, with metallic parts obtained with electroplating. In Gjokaj et al. [6], a Vivaldi antenna operating in the Ku band has been described as well as its manufacturing process, the so-called Polyjet 3D-printing. In this case, the metallization has been created with a first deposition by sputtering of a Titanium and Copper compound, then used as a base for an electroplating process. A different approach has been described in Jammes et al. [7], where a Jet Metal printing process has been used to produce a metal pyramidal horn antenna without the need to successively metalize anything. Similarly, in Reinhardt et al. [8] the production process of a corrugated pyramidal horn antenna has been entrusted to the Selective Laser Melting (SLM) technology. In particular, a prototype operating at 110 GHz has been realized melting Bronze powder and then plated with Gold. In Huang et al. [9] a similar technique called Direct Metal Laser Sintering (DMLS) has been used to realize a horn antenna prototype too, exploiting some Aluminum powder instead of the Bronze one. In Rojas-Nastrucci et al. [10] the Binder Jetting technology is described and used to develop a horn antenna operating in the Ka-band. Finally, in Shen et al. [11] the Digital Light Processing (DLP) has been used as production technology to manufacture some waveguide pieces easily and affordably with a very high resolution. Those pieces have then been metalized by exploiting the so-called Tollen’s reaction.
Based on an extension for a special issue of the work presented at the Splitech 2020 conference [12], this paper is focused on a comprehensive comparison between two of the most common and affordable 3D-printing techniques applied to the prototyping of electromagnetic structures. On the one hand, the FDM technique is taken into account. On the other hand, the DLP is considered. The former is based on the controlled extrusion of a fused polymeric filament which is used to build 3D objects layer by layer from bottom to top. The latter is based on the photocuring of a liquid resin which uses an LCD screen emitting UV light to harden the polymer with a resolution as high as the pixel dimension. To better describe the pros and cons of these technologies, a brief overview of the fundamental knowledge useful for applying 3D-printing in electromagnetics is provided. In this regard, the topic of the dielectric characterization of 3D-printable materials is faced. The theoretical principle behind the T-Resonator device is described by highlighting the main steps of its possible realization taking advantage of 3D-printing. Subsequently, some considerations about the use of FDM are pointed out by focusing the attention on its limits and potentials in electromagnetics. For instance, the most important drawback of commercial printable materials when used in electromagnetic applications is their relatively low dielectric constant (between 2 and 3). Some solutions to improve this value are presented and discussed. Finally, the possibilities offered by the use of an unconventional conductive filament called Electrifi [13] which is suitable for FDM-based electromagnetic applications are discussed.
On the other hand, DLP is described and identified as one of the promising AM technologies suitable for electromagnetic applications. The differences with FDM are pointed out in terms of electromagnetic properties of the printable materials, resolution, and accuracy as well as general costs. Two prototypes of a tunable Planar Inverted F Antenna (PIFA) for Ultra High Frequency (UHF) RFID applications have been produced with both the techniques, characterized under the electromagnetic point of view and critically discussed and compared.

### 2. Electromagnetic Characterization of 3D-Printable Materials through the

T-Resonator Method
In this section, a fundamental aspect of 3D-printing in electromagnetics is briefly summarized. This is the earliest problem that always arises when new materials are adopted to realize RF devices. That is the characterization of their electromagnetic properties in terms of permittivity (εr) and loss-tangent (tanδ). A way to face this problem is to use the so-called T-Resonator, which is a well-known structure whose behavior is described in the literature [14,15]. It can be used to obtain a measurement instrument, as detailed in Catarinucci et al. [16], adoptable also to characterize, among the others, 3D-printed substrates. Briefly, it consists of a two-port microwave circuit composed of a microstrip line with an open-end stub resonating at odd-integer multiples of its quarter-wavelength corresponding frequency. Both the εr and tanδ of the substrate under test can be determined with a specific elaboration, once the scattering parameter S21 is known. For this reason, a structure capable to place a certain pressure all over the “T”, while holding still the substrate under test, has been designed and 3D-printed using common Polylactic Acid (PLA) as 3D-printable material. Screw regulators are foreseen to assure the possibility to form a sandwich structure between the metallic parts and substrate of different thicknesses. More details about the T-Resonator realization can be found in Catarinucci et al. [16].
By using the T-resonator it is possible to demonstrate how the proper tuning of the 3D-printer parameters capable of setting the “infill percentage” of a 3D-printed substrate can lead to dielectric constant customizability. Indeed, the infill percentage is a value indicating the fraction of material over air used to fill the 3D model. An object printed with a low infill percentage has a greater percentage of air inside while maintaining its usual dimensions. Indeed, by properly setting this parameter, the dielectric constant and the loss tangent of the final printed element can be controlled according to the specific application. As an example, the dependency of the PLA dielectric parameters on the infill percentage is reported in Table 1. As expected, the lower is the infill percentage, the lower are the values of dielectric constant and loss tangent of the substrate under test.

Table 1. Dielectric PLA parameter with varying the infill percentage.

Infill % | εr | tanδ
20 | 1.503 | 0.0031
30 | 1.578 | 0.0034
40 | 1.646 | 0.0035
50 | 1.8 | 0.0043
60 | 1.942 | 0.0048
70 | 2.13 | 0.0051
80 | 2.25 | 0.0054
90 | 2.371 | 0.0062
100 | 2.541 | 0.0071

### 3. Fused Deposition Modelling in Electromagnetics

FDM is the most common 3D-printing technology and it has largely spread out in the last few years, due to the negligible cost of both printers and needed materials. It works realizing a plastic prototype extruding a melt polymeric filament through a tinny nozzle, which moves following a pattern and so drawing the proper layer shape. The final object is built layer by layer.
So far, a large literature related to the use of FDM in electromagnetics has been produced exploiting and exploring different aspects of this innovative technology. In addition to the already described works on it [1,2,16], more others could be cited. A not exhaustive list could contain Massoni et al. [17], where the authors have used the possibility to tune the infill of a model printed by FDM technology to realize a Substrate Integrated Slab Waveguide obtaining an enhanced bandwidth; Moscato et al. [18], where the same principle and the use of a special elastic material called Ninjaflex have been used to produce an unconventional antenna; Rocco et al. [19], in which the authors have described how they successfully manufactured a 3D-printed microfluidic sensor by exploiting a substrate integrated waveguide cavity; Martínez Odiaga et al. [20], where a particularly lightweight circular horn antenna for police radar application has been printed with FDM; Alkaraki et al. [21], in which authors reported the realization of a particular 3D-printed slot antenna operating in the Ka band. Eventually, in Helena et al. [22], a very accurate review on different AM technology (FDM among the others) applied in the prototyping of antennas, is proposed.
To summarize, the most interesting possibility is to prototype any kind of unconventionally-shaped electromagnetic structure, in a fraction of the time and with a lower cost than the standard manufacturing technologies.
On the other hand, one of the most important drawbacks is that, as already stated, the common commercial filaments exhibit a relatively low value of dielectric constant (between 2 and 3), and this could be not high enough in some applications where, for instance, antenna miniaturization is needed. Other problems regard the typical accuracy of an FDM printing process, which lays around 0.2 mm. In fact, although this value could be thought low enough at low frequencies, it starts to generate potential problems while increasing the frequency, especially if it affects the roughness of the conductive parts of the device. Eventually, the possibility to realize electromagnetic devices (with both dielectric and conductive parts) only using FDM 3D-printing needs to be considered. Indeed, even if this technology allows to print only thermoplastic materials, innovative filaments with conductive properties have been recently developed and commercialized as described below. There are two possible approaches to fulfill the need for printable devices with higher dielectric constants. The former is to take advantage of all the benefits of a shape freely designable by realizing a 3D-printed mold with standard material and then cast it with a specific compound material opportunely realized to exhibits the needed dielectric properties. The latter is to produce advanced filaments for FDM 3D-printing that overcome the limits of the standard ones. Both are described below along with the direct 3D-printing of conductive materials.
The “mold technique” is a particular method useful when flexible devices are designed. It consists in the realization of a silicone rubber compound, which is electromagnetically enhanced by adding highly dielectric powders and subsequently shaped through 3D-printed molds. One of the ceramic powders mostly used for this kind of mixture is the Barium Titanate (BaTiO3), already used in literature for this purpose [23] because it is a strong ferroelectric material (with a very high dielectric constant). The dielectric properties of the mixed compound can be well forecast through Lichtenecker’s equation which describes a logarithmic connection between the complex permittivity of the matrix material and that of the doping one, as can be seen in Equation (1):

log εe f f = log εmatrix + ϕ log

εf iller/εmatrix
, | (1)

where εeff is the resulting permittivity of the compound, εmatrix and εfiller are the permittivity of the matrix and the filler materials, respectively, and eventually, ϕ is the volume fraction of the filler in the whole composite.
As an example of the results achievable with this technique, in Figure 1a the labmade RFID tag, described in Catarinucci et al. [24], is shown. It has been realized with a compound of silicone rubber and BaTiO3 and has been modeled through a braceletshape mold.
As for the second technique based on the definition of advanced filaments with increased electromagnetic properties, such materials are realized by extruding a specific ceramic-doped 3D-printable plastic mixture. Similar to the previous case, the main idea consists again in increasing the dielectric constant of a base material by adding highly dielectric powders. This technique has been previously used to realize an ABS filament doped with BaTiO3 as reported in Yingwei et al. and Castles et al. [25,26]. Conversely, the authors of the present work experienced the PLA as a matrix instead of ABS, because of its greater ease of print.
Even in this case, Lichtenecker’s equation can proficiently forecast the final dielectric constant, which is revealed to be, at the same percentage of doping agent, slightly lower than the one obtained by using silicone rubber. This is obviously due to the lower starting value of the dielectric constant of the PLA (~2.5 for PLA vs. ~3.2 for silicone).

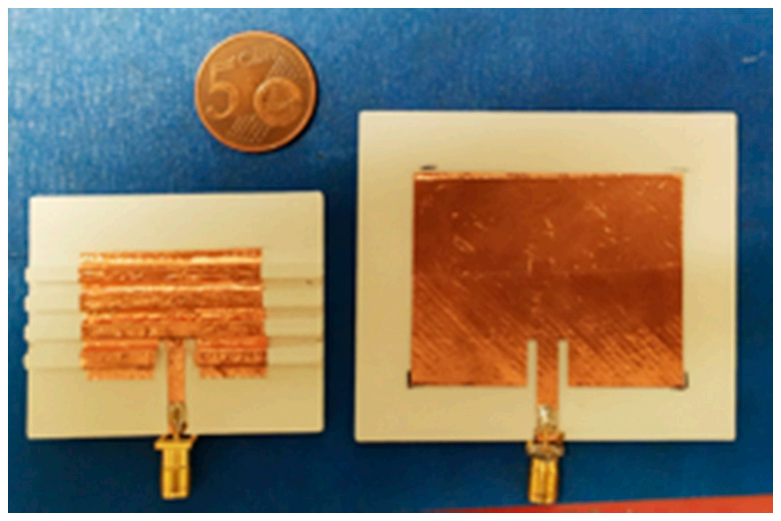
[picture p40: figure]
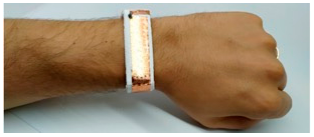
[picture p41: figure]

(a) (b)

Figure 1. (a) Prototype of a ultra high frequency (UHF) radiofrequency Identification (RFID) tag for on-body application realized with the molding technique [10]. (b) 2.4 GHz patch antenna made with standard PLA (right) and reduced size patch antenna printed in BaTiO3 enhanced PLA with meandered design (left).

The outcome is a printable filament that achieves εr ' 4.6 and tanδ ' 0.015 for a doping percentage of 17.5% of the total volume. This is a remarkable result considering that the dielectric constant of a standard PLA has been almost doubled maintaining acceptable values for the losses. As an example of application, in Figure 1b comparison between a 2.4 GHz patch antenna realized with common PLA and one printed using the BaTiO3 enhanced PLA joint with a particular meandered design for the patch radiating element, is shown. It is clear how the improved dielectric constant and the clever design guarantees a considerable size reduction of the antenna.
In addition to the above-discussed techniques to improve the material permittivity, one of the most interesting possibilities enabled by 3D-printing is to extrude the conductive parts to obtain novel fully 3D-printed electromagnetic devices, without the need for other techniques to produce the metallic parts. Obviously, the main type of material which is usable by the desktop 3D-printers is a polymer that is naturally not a conductor. Nevertheless, in the last few years, some unconventional hybrid materials, composed of polymer and nanoparticles of conductors, have been developed and commercialized. One of the most promising is Electrifi, which is produced by Multi3D [13]. With a declared conductivity of 1.6 × 10⁴ S/m, and a measured one ranging from 1.2 × 10³ S/m to 8.3 × 10³ S/m (it depends on the printing settings and the measurement direction), it revealed to be a good enough conductor for realizing fully 3D-printed RF devices.
As an example of the achievable results, one of the first prototypes of a fully 3D-printed patch antenna, operating at around 2.4 GHz and printed in Electrifi and PLA, is shown in Figure 2a. This structure is better discussed in Colella et al. [27], while the prototype of similarly realized UHF RFID antenna is shown in Figure 2b and deeply compared with other similar-layout tags in Colella et al. [28].

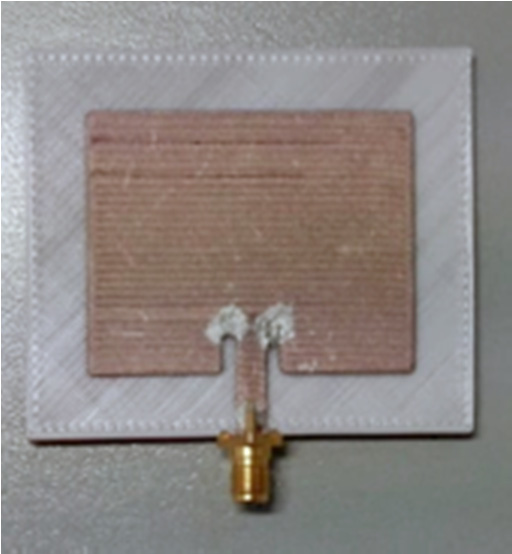
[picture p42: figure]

(a) (b)

Figure 2. (a) Fully 3D-printed 2.4 GHz patch antenna made of PLA (substrate) and Electrifi (antenna) [13]. (b) Fully 3D-printed UHF RFID tag made of PLA (substrate) and Electrifi (antenna) [28].

### 4. Digital Light Processing in Electromagnetics

As stated, the most common technology for 3D-printing prototyping and, hence, for 3D-printing in electromagnetics, is the FDM one. However, it is not the only affordable one. In fact, especially in the last few years, the resin-based (also known as vat polymerization) 3D-printing technology has spread out also in the consumer market. Specifically, the cost of these types of printers has dropped down with the advent of Digital Light Processing (DLP). It briefly consists of the photopolymerization of the resin using a UV light emitted by a cost-effective high-resolution display. Hence, the substitution of the most common and expansive light source (which, for example, is a laser in SLA 3D-printers or a projector in another type of DLP machines) as well as the consequent simplification of the required mechanic, led to a consistent drop of the costs maintaining the quality guaranteed by the resin-based 3D-printing techniques. DLP, indeed, allows one to achieve a level of accuracy in the model realization even 10 times higher than the FDM one. This characteristic is particularly appreciable when a complex geometry is required. Moreover, a lowerdimensional tolerance is an added value in microwave device realization, where even little discrepancies between the simulated and the realized device could lead to not tolerable errors (typically when frequencies are over 10 GHz and surface roughness of the device affects the conductivity).
As for the printable materials for FDM technology, the authors have made a preliminary study to characterize the dielectric properties of one common commercial DLP resin (Anycubic Green 405 nm) [23]. An Anycubic Photon-S DLP 3D printer (see Figure 3a) has been used to produce a 40 × 80 × 1.6 mm³
substrate, using an Anycubic 405 nm resin. Then, a copper adhesive tape has been shaped into a properly dimensioned “T” (considering the substrate height the microstrip width has been set to be 4.2 mm) through a cutting plotter and subsequently applied to the previously printed substrate, so to obtain the resonator shown in Figure 3b.

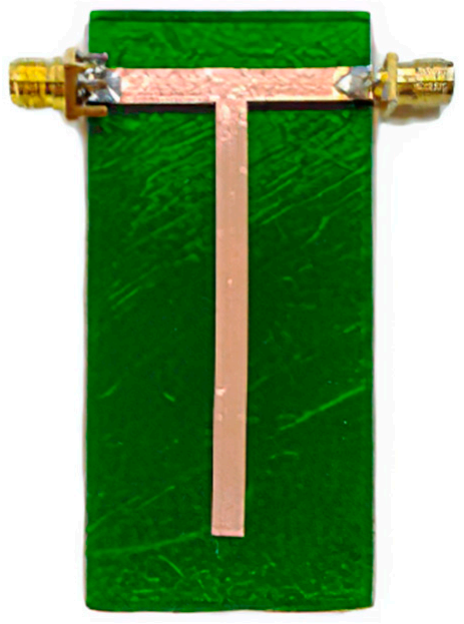
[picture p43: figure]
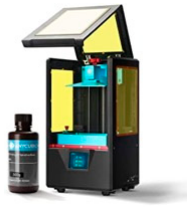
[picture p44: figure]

(a) (b)

Figure 3. (a) Digital Light Processing (DLP) 3D-printer Anycubic Photon-S with its own 405 nm resin. (b) Resin-made T-Resonator printed with a DLP 3D printer.

The 52 mm length of the stub allows one to measure the dielectric properties of the polymer at a frequency around 800 MHz, near the working band of the UHF RFID technology, on which the further described application is focused. Specifically, values of εr = 3.11 and tanδ = 0.033 have been obtained.

### 5. Analysis of FDM and DLP Technologies in Electromagnetics

Analyzing the main properties of the 3D-printing technologies described in the previous sections, it is possible to compare them in terms of the electromagnetic properties of the printable materials, resolution of the final printed parts and, general costs. After this theoretical comparison, a more practical one is carried out by confronting two UHF RFID tunable antennas realized with the same conceptual design but using the two different rapid prototyping methods.

5.1. Electromagnetic Properties of the Printable Materials
Comparing the results obtained by the dielectric characterization, through the T-Resonator method, of both common DLP and FDM materials it is clear how the resin exhibits a higher value for dielectric constant, but also for loss tangent. However, even if the losses of this specific resin resulted relatively high, they are nevertheless compatible with a real application and the use of DLP remains appealing since it allows to realize geometries that are unprintable otherwise.
The possibility of making improved versions of printable materials by adding, for example, ceramic powder to the polymer matrix is a viable path for both techniques. Specifically, in the case of FDM, it is possible to realize a printable filament as stated in Section 3, while for the DLP technique a mix of resin and powder can be used instead of simple resin to photopolymerize the model [29]. In the latter case, different printing settings must be used to successfully compensate for the minor penetration distance of the light in a compound doped with an opaque powder. A good starting point could be to enhance of 50% the curing time of both the firsts model layers (which have to attach robustly to the moving bed of the printer) as well as the following ones.
5.2. Resolution and Accuracy
To successfully understand the difference in accuracy between the two techniques, it is useful to understand which are the elements that affect it. For example, in FDM the two main elements that determine the printing accuracy are the nozzle diameter (ranging from 0.1 to 1 mm) and the layer height (approximately ranging from 0.08 to 0.64 mm). The former affects the surface roughness of the material (along the XY plane), the latter affects the roughness along the z-axis. Moreover, while the latter can be easily taken low, paying accuracy with printing-time, the former is a parameter not so easily tunable. In fact, a lot of materials cannot be printed through a too-small nozzle, and for this reason, the highest accuracy for an FDM 3D-printer is considered to be around 0.2 mm.
Conversely, the DLP has a single moving part, which is the z-axis stepper that moves the printing bed. A typical value for the accuracy of this stepper is 0.0125 mm. On the other hand, the accuracy on the XY plane is given by the size of the LCD pixels, which for the DLP printer used by authors is 0.047 mm.
Finally, as for the roughness of the printed surface, it has to be considered that it is the same as the Fluorinated Ethylene Propylene (FEP) film that is used as vat bottom surface of the DLP 3D-printer. This allows DLP printers to produce models with very smooth surfaces if compared with that realized with an FDM process (a more detailed analysis is performed in the “Results” Section).
5.3. General Costs
The strength of modern AM technologies like FDM and DLP is the very low costs of both printers and materials. For example, the FDM 3D-printer used to realize the prototypes proposed in this work is purchasable for about $200, while for less than $400, it is possible to buy a DLP 3D-printer. As for the consumables, the cost of a spool of filament for FDM ranges from $20 to $200, depending on the material properties. Even for a bottle of resin for DLP a similar amount of money is needed. This makes these AM techniques appealing for rapid prototyping at a fraction of the cost and time of standard production methods.

### 6. UHF RFID Tunable Antennas: Design and Realization

A particular type of PIFA layout has been designed and simulated in CST Microwave Studio. A self-explaining rendered image can be observed in Figure 4. Briefly, the device is composed of 2 elements: the body, where the radiating element, as well as the feeding line and the background plane, are placed, and the sliding ring, which wraps around the body and has copper attached on its inner side. The body can float inside the ring, while the copper on it acts as shorting wall for the PIFA. The movement allows to vary the distance between the shorting wall and the feeding line of the antenna, thus determining a tuning procedure that can proficiently adapt the antenna parameters depending on the needed application. It is worth highlighting that a similar layout is enabled by the 3D-printing technology.

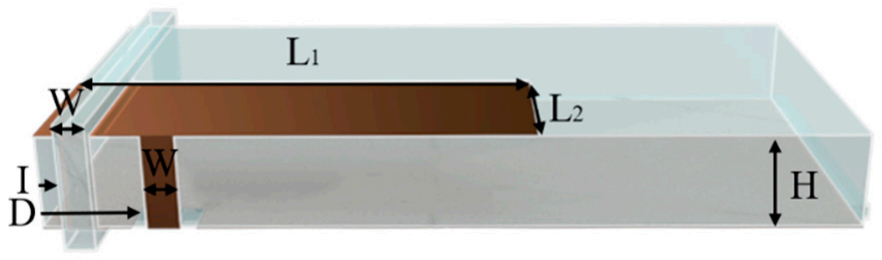
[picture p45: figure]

(a)

(b) (c)

Figure 4. Rendered image of the designed Planar Inverted F Antenna (PIFA) antenna. (a) Prospective view. (b) Top view. (c) Bottom view.

It is worth highlighting that the prototype printed with the DLP printer has been realized using a common commercial resin. Conversely, a particular built-in-lab filament composed of PLA doped with a 17.5% volume fraction of BaTiO3 has been used for the prototype realized with FDM technology. The filament has been produced mixing and extruding at the same time the Ingeo 4043D (NatureWorks, Minnetonka, MN, USA) PLA pellet with a BaTiO3-325 mesh powder pure at 99%, through a twin-screw extruder. The doping percentage has been selected to have a good compromise between dielectric constant increment and ease of printing. Indeed, as the amount of BaTiO3 increases, the brittleness increases as well, and the ease of flow of the material is reduced. This mix guarantees a dielectric constant of 4.8 at around 900 MHz and a loss tangent of 0.015 for the substrate of the antenna, helping to reduce antenna size if compared with a standard PLA substrate, as well as making the device more platform tolerant.
Conversely, the prototype made with the commercial resin, exhibiting a lower value of dielectric constant (3.11), had a larger size (see Table 2). Moreover, without loss of generality, for the DLP prototype, an additional brace has been added to the ring part so to better ensure the stiffness of the prototype.

Table 2. Design parameters of the two different antenna prototypes (size in [mm]).

Parameters | DLP | FDM
L1 | 36.6 | 30.5
L2 | 11.6 | 10.5
W | 2.4 | 2
I | 0.9 1/2.7 2 | 1.2 1/3.2 2
D | 7.8 | 6.5
H | 6 | 6
1 For the configuration operating in the European Telecommunications Standards Institute (ETSI) band. 2 For the configuration operating in the Federal Communications Commission (FCC) band

As for the metallic parts of the antennas, they have been realized with a tiny copper adhesive tape-shaped using a Graphtec ce6000-40 (Graphtech Corporation, Tokyo, Japan) cutting plotter [30]. In Figure 5 the two realized prototypes are shown.

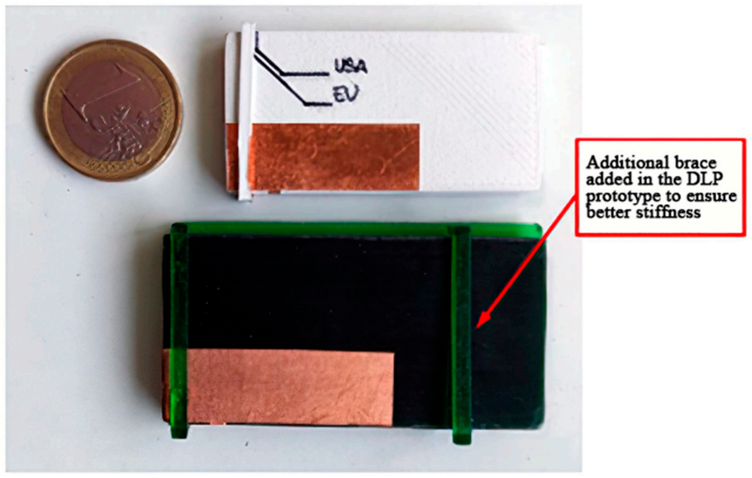
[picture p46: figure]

Figure 5. Final 3D-printed prototypes of the UHF RFID PIFA inspired antenna.

Eventually, as for the internal chip (IC), The simulation phase has been aimed at optimizing the parameters of the antennas to match the impedance of the Impinj Monza R6 chip (Impinj, Seattle, WA, USA) [31].

### 7. Results

First of all, to take into account all possible differences between the two realization techniques, a roughness measure has been made as shown in Figure 6, where two roughness profiles of respectively an FDM and a DLP 3D-printed sample are shown. They have been measured with a Veeco Dektak 150 (Veeco, Plainview, NY, USA) equipped with a 12.5 nm stylus and the compared profiles have been chosen to be the ones with the highest values (so to consider the worst case). As can be easily seen, the DLP sample has a roughness of barely one order of magnitude lower than the FDM sample. Specifically, the RMS values for both the profiles are respectively 2.15 µm for the DLP and 12.82 µm for the FDM. Nevertheless, these values are barely negligible if a UHF RFID application is developed, because they are hugely smaller than the wavelength at working frequencies. For this reason, simulations have been performed without taking the roughness of the material into account.

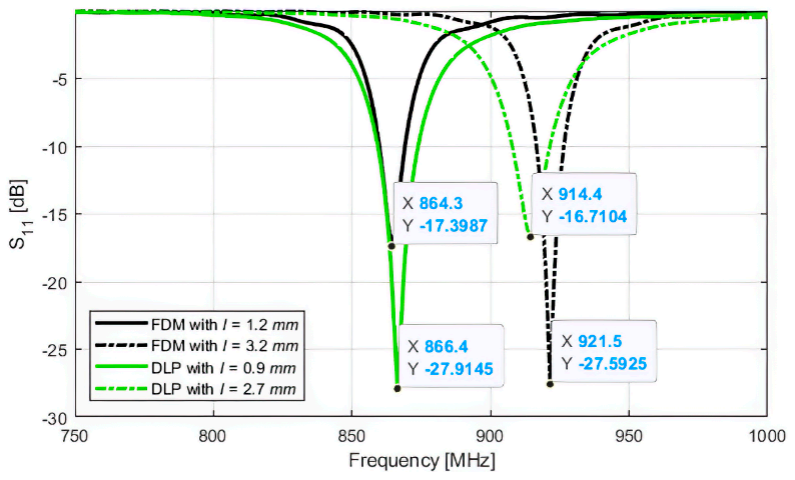
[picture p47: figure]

Figure 6. Comparison between Fused Deposition Modelling (FDM) and DLP roughness profiles.

For both the antennas, the S11 curve for the two different configurations of the tag, corresponding to different positions of the wrapping ring (referred to the different values of parameter I in Table 2), have been simulated as shown in Figure 7. As can be seen, each antenna exhibits two points of good matching, respectively for working in the ETSI or FCC bands. These simulations have been confirmed by the sensitivity measurements that have been used to have a snapshot of the two tags’ performance with varying frequency.

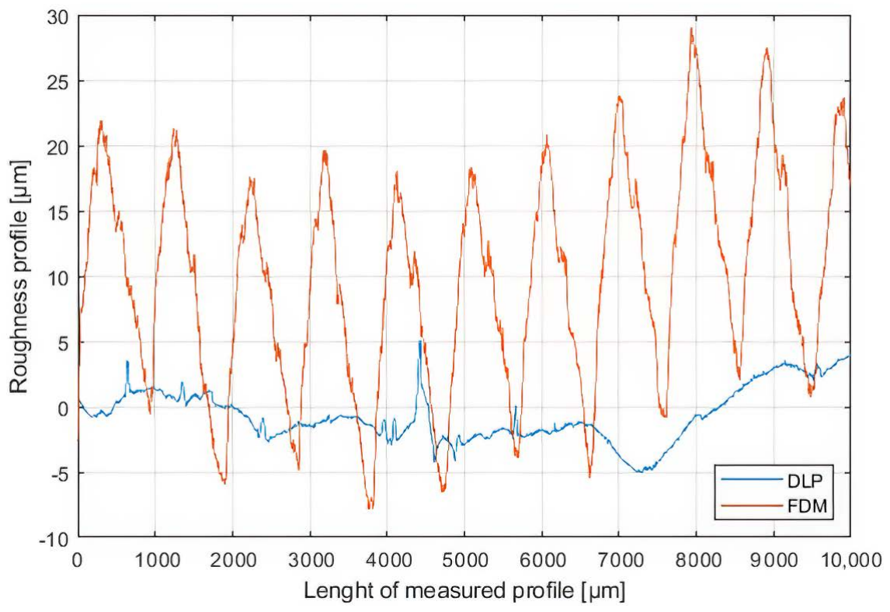
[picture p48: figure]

Figure 7. Comparison between the simulated S11 curves for the antennas in both the working configurations.

The measurements have been made using the built-in-lab instrument described in Colella et al. [32] and the results in terms of sensitivity as well as maximum reading distance curves are shown in Figures 8 and 9. Analyzing the curves, it is clear how the change in the position of the ring part of the antennas, undoubtedly determines a tune of the antenna impedance which allows it to operate correctly at the selected frequency. Moreover, a slightly better performance is obtained by the antenna printed with the FDM method, despite its smaller size. This is probably due to the lower value of loss-tangent of the used filament (~0.015) that is barely half the one of the commercial resin (Anycubic Green 405 nm) used for the DLP prototype (~0.033).

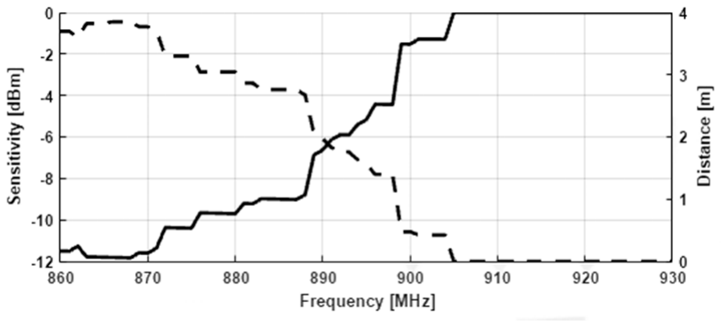
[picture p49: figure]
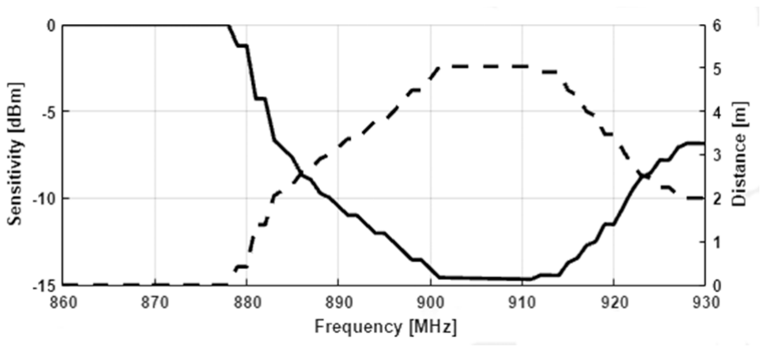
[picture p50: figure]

(a) (b)

Figure 8. Sensitivity and maximum reading distance for FDM 3D-printed prototype, respectively for ETSI (a) and FCC band (b).

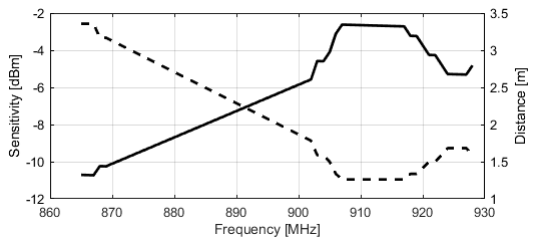
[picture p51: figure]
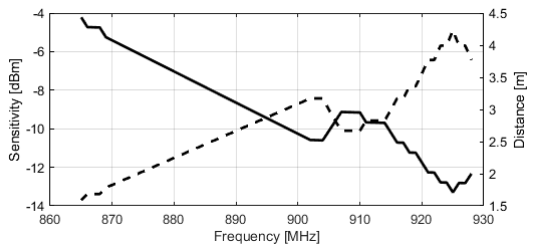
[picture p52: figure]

(a) (b)

Figure 9. Sensitivity and maximum reading distance for DLP 3D-printed prototype, respectively for ETSI (a) and FCC band (b).

### 8. Comments and Future Directions

The sensitivity and maximum reading distance described in the previous section allow one to state that both the examined AM technologies can be suitable for realizing electromagnetic devices with similar performance, at least at the UHF RFID frequencies. Nevertheless, the two technologies have not to be considered interchangeable. There are indeed many differences between them that must be considered when choosing one over the other to realize a specific RF application. For example, when higher frequency applications are needed the difference in resolution could play a major role, especially if it impacts the roughness of the conductive parts of the device. Moreover, considerations about losses must be also considered. The commercial resins seem to show higher losses if compared with commercial FDM filaments; however, an improvement of their electromagnetic properties by using for instance high dielectric constant and low losses ceramic powders as filler deserves to be further investigated.
On the other hand, FDM takes advantage of the larger diffusion and of the longer research effort of the scientific community to improve it from the electromagnetic point of view. This determines a larger variety of materials and techniques available for it which, for example, makes it possible to print flexible or elastic structures (using materials as the so-called Ninjaflex [33]), or fully 3D-printed conductive parts (using for instance the Electrifi [13]).
There is no doubt that, despite its current limits, DLP technology has the potential to contribute to the realization of 3D-printed electromagnetic devices, overcoming the resolution limits of the more widespread FDM technology. However, dedicated research is needed to make new materials, techniques, and procedures suitable for electromagnetic projects available for DLP technology.

### 9. Conclusions

In this paper, a comparison between the two most used and cheap 3D-printing techniques is carried out highlighting the most useful aspects from the electromagnetic point of view. Other than a recap of the fundamentals of 3D-printing in electromagnetics and a theoretical discussion about the differences between FDM and DLP, a more practical comparison has been proposed. Specifically, it consists of the analysis of the performance of two prototypes of the same tunable PIFA antenna, designed for UHF RFID applications and realized with both the rapid prototyping methods under test.
In the end, the results have been commented on and used to discuss the potential of the research activity in the framework of 3D-printing of electromagnetics, as well as its future development.

Author Contributions: Funding acquisition, L.C.; Supervision, R.C. and L.C.; Validation, F.P.C.; Writing—original draft, F.P.C. and L.C.; Writing—review & editing, R.C. and F.P.C. All authors have read and agreed to the published version of the manuscript.

Funding: This research received no external funding.

Institutional Review Board Statement: Not applicable.

Informed Consent Statement: Not applicable.

Data Availability Statement: The data presented in this study are available on request from the corresponding author.

Conflicts of Interest: The authors declare no conflict of interest.

References
1. Farooqui, M.F.; Kishk, A. 3-D-Printed Tunable Circularly Polarized Microstrip Patch Antenna. IEEE Antennas Wirel. Propag. Lett. 2019, 18, 1429–1432. [CrossRef] (http://doi.org/10.1109/LAWP.2019.2919255)
2. Fenn, A.J.; Pippin, D.J.; Lamb, C.M.; Willwerth, F.G.; Aumann, H.M.; Doane, J.P. 3D printed conformal array antenna: Simulations and measurements. In Proceedings of the 2016 IEEE International Symposium on Phased Array Systems and Technology (PAST), Waltham, MA, USA, 18–21 October 2016; pp. 1–4.
3. Heirons, J.; Jun, S.; Shastri, A.; Sanz-Izquierdo, B.; Bird, D.; Winchester, L.; Evans, L.; McClelland, A. Inkjet printed GPS antenna on a 3D printed substrate using low-cost machines. In Proceedings of the 2016 Loughborough Antennas & Propagation Conference (LAPC), Loughborough, UK, 14–15 November 2016; pp. 1–4.
4. Mirmozafari, M.; Saeedi, S.; Saeidi-Manesh, H.; Zhang, G.; Sigmarsson, H.H. Direct 3-D Printing of Nonplanar Linear-Dipole-Phased Array Antennas. IEEE Antennas Wirel. Propag. Lett. 2018, 17, 2137–2140. [CrossRef] (http://doi.org/10.1109/LAWP.2018.2860463)
5. Kaddour, A.S.; Bories, S.; Bellion, A.; Delaveaud, C. 3D printed compact dual-polarized wideband antenna. In Proceedings of the 2017 11th European Conference on Antennas and Propagation (EUCAP), Paris, France, 19–24 March 2017; pp. 3441–3443.
6. Gjokaj, V.; Chahal, P.; Papapolymerou, J.; Albrecht, J.D. A novel 3D printed Vivaldi antenna utilizing a substrate integrated waveguide transition. In Proceedings of the 2017 IEEE International Symposium on Antennas and Propagation & USNC/URSI National Radio Science Meeting, San Diego, CA, USA, 9–14 July 2017; pp. 1253–1254.
7. Jammes, A.; des Gayets, E.; Staelens, K.; Feger, R.; Lampersberger, T.; Stelzer, A. Silver metallization of 77 GHz 3D printed horn antennas. In Proceedings of the 12th European Conference on Antennas and Propagation (EuCAP 2018), London, UK, 9–13 April 2018; pp. 1–4.
8. Reinhardt, A.; Möbius-Labinski, M.; Asmus, C.; Bauereiss, A.; Höft, M. Additive Manufacturing of 300 GHz Corrugated Horn Antennas. In Proceedings of the 2019 IEEE MTT-S International Microwave Workshop Series on Advanced Materials and Processes for RF and THz Applications (IMWS-AMP), Bochum, Germany, 16–18 July 2019; pp. 40–42.
9. Huang, G.; Zhou, S.; Chio, T. Lightweight perforated horn antenna enabled by 3-D metal-direct-printing. In Proceedings of the 2016 IEEE International Symposium on Antennas and Propagation (APSURSI), Fajardo, Puerto, 26 June–1 July 2016; pp. 481–482.
10. Rojas-Nastrucci, E.A.; Nussbaum, J.; Weller, T.M.; Crane, N.B. Metallic 3D printed Ka-band pyramidal horn using binder jetting. In Proceedings of the 2016 IEEE MTT-S Latin America Microwave Conference (LAMC), Puerto Vallarta, Mexico, 12–14 December 2016; pp. 1–3.
11. Shen, J.; Ricketts, D.S. 3D Printing of Complex, High-Performance Millimeter-Wave Components. In Proceedings of the 2020 IEEE Radio and Wireless Symposium (RWS), San Antonio, TX, USA, 20–23 January 2020; pp. 27–30.
12. Colella, R.; Chietera, F.P.; Catarinucci, L. Digital Light Processing as One of the Promising 3D-Printing Technologies in Electromagnetics: Application on RFID. In Proceedings of the 2020 5th International Conference on Smart and Sustainable Technologies (SpliTech), Split, Croatia, 23–26 September 2020; pp. 1–4.
13. Electrifi by Multi3Dllc Info Page. Available online: https://www.multi3dllc.com (accessed on 4 April 2020).
14. Latti, K.P.; Kettunen, M.; Stoem, J.-P.; Silventoinen, P. A review of microstrip T-resonator method in determining the dielectric properties of printed circuit board materials. IEEE Trans. Instrum. Meas. 2007, 56, 1845–1850.
15. Collin, R.E. Foundations for Microwave Engineering; Wiley: Hoboken, NJ, USA, 1985.
16. Catarinucci, L.; Colella, R.; Coppola, P.; Tarricone, L. Microwave characterisation of polylactic acid for 3D-printed dielectrically controlled substrates. IET Microw. Antennas Propag. 2017, 11, 1970–1976. [CrossRef] (http://doi.org/10.1049/iet-map.2017.0498)
17. Massoni, E.; Silvestri, L.; Alaimo, G.; Marconi, S.; Bozzi, M.; Perregrini, L.; Auricchio, F. 3-D Printed Substrate Integrated Slab Waveguide for Single-Mode Bandwidth Enhancement. IEEE Microw. Wirel. Compon. Lett. 2017, 27, 536–538. [CrossRef] (http://doi.org/10.1109/LMWC.2017.2701323)
18. Moscato, S.; Bahr, R.; Le, T.; Pasian, M.; Bozzi, M.; Perregrini, L.; Tentzeris, M.M. Infill-Dependent 3-D-Printed Material Based on NinjaFlex Filament for Antenna Applications. IEEE Antennas Wirel. Propag. Lett. 2016, 15, 1506–1509. [CrossRef] (http://doi.org/10.1109/LAWP.2016.2516101)
19. Rocco, G.M.; Bozzi, M.; Schreurs, D.; Perregrini, L.; Marconi, S.; Alaimo, G.; Auricchio, F. 3-D Printed Microfluidic Sensor in SIW Technology for Liquids’ Characterization. IEEE Trans. Microw. Theory Tech. 2020, 68, 1175–1184. [CrossRef] (http://doi.org/10.1109/TMTT.2019.2953580)
20. Odiaga, H.J.M.; Medina, M.A.Y.; Navarro, S.A. An Implemented 3D Printed Circular Waveguide Antenna for K Band Applications. In Proceedings of the 2018 IEEE MTT-S Latin America Microwave Conference (LAMC 2018), Arequipa, Peru, 26–28 May 2018; pp. 1–3.
21. Alkaraki, S.; Andy, A.S.; Gao, Y.; Tong, K.; Ying, Z.; Donnan, R.; Parini, C. Compact and Low-Cost 3-D Printed Antennas Metalized Using Spray-Coating Technology for 5G mm-Wave Communication Systems. IEEE Antennas Wirel. Propag. Lett. 2018, 17, 2051–2055. [CrossRef] (http://doi.org/10.1109/LAWP.2018.2848912)
22. Helena, D.; Ramos, A.; Varum, T.; Matos, J.N. Antenna Design Using Modern Additive Manufacturing Technology: A Review. IEEE Access 2020, 8, 177064–177083. [CrossRef] (http://doi.org/10.1109/ACCESS.2020.3027383)
23. Koulouridis, S.; Kiziltas, G.; Zhou, Y.; Hansford, D.J.; Volakis, J.L. Polymer-Ceramic Composites for Microwave Applications: Fabrication and Performance Assessment. IEEE Trans. Microw. Theory Tech 2006, 54, 4202–4208. [CrossRef] (http://doi.org/10.1109/TMTT.2006.885887)

24. Catarinucci, L.; Chietera, F.P.; Colella, R. Permittivity-Customizable Ceramic-Doped Silicone Substrates Shaped with 3D-Printed Molds to Design Flexible and Conformal Antennas. IEEE Trans. Antennas Propag. 2020, 68, 4967–4972. [CrossRef] (http://doi.org/10.1109/TAP.2020.2969748)
25. Wu, Y.; Isakov, D.; Grant, P.S. Fabrication of Composite Filaments with High Dielectric Permittivity for Fused Deposition 3D Printing. Materials 2017, 10, 1218. [CrossRef] (http://doi.org/10.3390/ma10101218) [PubMed] (http://www.ncbi.nlm.nih.gov/pubmed/29065537)
26. Castles, F.; Isakov, D.; Lui, A.; Lei, Q.; Dancer, C.E.J.; Wang, Y.; Janurudin, J.M.; Speller, S.C.; Grovenor, C.R.M.; Grant, P.S. Microwave dielectric characterisation of 3D-printed BaTiO 3/ABS polymer composites. Sci. Rep. 2016, 6, 22714. [CrossRef] (http://doi.org/10.1038/srep22714) [PubMed] (http://www.ncbi.nlm.nih.gov/pubmed/26940381)
27. Colella, R.; Chietera, F.; Catarinucci, L.; Casula, A.; Montisci, G.; Gatto, G.; Michel, A.; Nepa, P.; Rogier, H. Electromagnetic Analysis and Performance Comparison of Fully 3D-printed Antennas. In Proceedings of the 2019 PhotonIcs & Electromagnetics Research Symposium—Spring (PIERS-Spring), Rome, Italy, 17–20 June 2019; pp. 964–970.
28. Colella, R.; Chietera, F.P.; Catarinucci, L.; Salmeron, J.F.; Rivadeneyra, A.; Carvajal, M.A.; Palma, A.J.; Capitán-Vallvey, L.F. Fully 3D-Printed RFID Tags based on Printable Metallic Filament: Performance Comparison with other Fabrication Techniques. In Proceedings of the 2019 IEEE-APS Topical Conference on Antennas and Propagation in Wireless Communications (APWC), Granada, Spain, 9–13 September 2019; pp. 253–257.
29. He, R.; Liu, W.; Wu, Z.; An, D.; Huang, M.; Wu, H.; Jiang, Q.; Ji, X.; Wu, S.; Xie, Z. Fabrication of complex-shaped zirconia ceramic parts via a DLP- stereolithography-based 3D printing method. Ceram. Int. 2018, 44, 3412–3416. [CrossRef] (http://doi.org/10.1016/j.ceramint.2017.11.135)
30. Graphtec ce6000-Series Cutting Plotter Datasheet. Available online: http://www.graphtec.co.jp/site_download/02_manual/data/CE6000_UserManual(CE6000-UM-154).pdf (http://www.graphtec.co.jp/site_download/02_manual/data/CE6000_UserManual(CE6000-UM-154).pdf) (accessed on 22 January 2021).
31. Impinj Monza R6 RFID Chip Info Page. Available online: https://support.impinj.com/hc/en-us/articles/202765328-Monza-R6 -Product-Brief-Datasheet (https://support.impinj.com/hc/en-us/articles/202765328-Monza-R6-Product-Brief-Datasheet) (accessed on 22 January 2021).
32. Colella, R.; Chietera, F.P.; Catarinucci, L. Electromagnetic Performance Evaluation of UHF RFID Tags with Power Discretization Error Cancellation. IEEE Trans. Antennas Propag. 2019, 67, 3545–3549. [CrossRef] (http://doi.org/10.1109/TAP.2019.2902708)
33. Filaflex Datasheet. Available online: http://3dfilaprint.com/ninjatek-ninjaflex-technical-data-sheet-2016/ (accessed on 22 January 2021).

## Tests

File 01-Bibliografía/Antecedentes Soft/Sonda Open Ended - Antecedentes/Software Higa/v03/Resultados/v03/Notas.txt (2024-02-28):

AGUA 25 (es 110)
=======
294 The iteration is not making good progress, as measured by the 
  improvement from the last five Jacobian evaluations.
354 The iteration is not making good progress, as measured by the 
  improvement from the last five Jacobian evaluations.
355 The iteration is not making good progress, as measured by the 
  improvement from the last five Jacobian evaluations.
356 The iteration is not making good progress, as measured by the 
  improvement from the last ten iterations.
358 The iteration is not making good progress, as measured by the 
  improvement from the last five Jacobian evaluations.

AGUA 40 (es 105)
=======
259 The iteration is not making good progress, as measured by the 
  improvement from the last five Jacobian evaluations.
277 The iteration is not making good progress, as measured by the 
  improvement from the last five Jacobian evaluations.
295 The iteration is not making good progress, as measured by the 
  improvement from the last five Jacobian evaluations.
354 The iteration is not making good progress, as measured by the 
  improvement from the last five Jacobian evaluations.
356 The iteration is not making good progress, as measured by the 
  improvement from the last five Jacobian evaluations.
360 The iteration is not making good progress, as measured by the 
  improvement from the last five Jacobian evaluations.
363 The iteration is not making good progress, as measured by the 
  improvement from the last five Jacobian evaluations.

AGUA 60 (es 98)
=======
297 The iteration is not making good progress, as measured by the 
  improvement from the last five Jacobian evaluations.
298 The iteration is not making good progress, as measured by the 
  improvement from the last five Jacobian evaluations.
338 The iteration is not making good progress, as measured by the 
  improvement from the last ten iterations.
352 The iteration is not making good progress, as measured by the 
  improvement from the last five Jacobian evaluations.
356 The iteration is not making good progress, as measured by the 
  improvement from the last five Jacobian evaluations.
357 The iteration is not making good progress, as measured by the 
  improvement from the last five Jacobian evaluations.
364 The iteration is not making good progress, as measured by the 
  improvement from the last five Jacobian evaluations.

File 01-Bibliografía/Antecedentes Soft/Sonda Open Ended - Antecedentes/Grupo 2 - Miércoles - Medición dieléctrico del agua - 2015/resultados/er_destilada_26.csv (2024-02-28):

80,2983315107 | -0,933479143884 | 93,3273362642 | -3,29542451816e-15
80,2971356965 | -0,980137406017 | 71,8588062755 | -3,30198276975
80,2958815911 | -1,02679337188 | 86,0284751122 | -3,75560684565
80,2945692003 | -1,07344693226 | 99,6950453906 | 3,80515703246e-16
80,2931985303 | -1,12009797795 | 83,1992492466 | -0,383982219608
80,2917695875 | -1,1667463998 | 78,468697908 | -1,96380899176
80,2902823786 | -1,21339208865 | 97,3831726978 | -2,83674363994
80,2887369105 | -1,26003493536 | 89,4410670472 | -0,801027115423
80,2871331905 | -1,30667483083 | 79,3505846478 | -1,52427193169
80,2854712261 | -1,35331166597 | 89,1093801812 | -6,74572409732
80,283751025 | -1,39994533172 | 92,7886170818 | -1,4613358257
80,2819725954 | -1,44657571904 | 82,9703372428 | -1,18059476275
80,2801359456 | -1,49320271891 | 79,8295539055 | -7,4306363323
80,2782410842 | -1,53982622236 | 94,8036371542 | -2,4240194799
80,2762880199 | -1,58644612042 | 85,9630236848 | -1,10406960635
80,2742767621 | -1,63306230417 | 78,9829447378 | -2,73603966257
80,27220732 | -1,6796746647 | 97,0131190644 | -2,61566658194
80,2700797035 | -1,72628309314 | 88,8236737038 | -0,554010694497
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

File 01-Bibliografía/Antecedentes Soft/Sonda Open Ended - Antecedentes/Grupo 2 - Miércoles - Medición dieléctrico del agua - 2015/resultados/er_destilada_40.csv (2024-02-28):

69,9899421965 | -0,804624277457 | 88,7619983417 | 1,17003932268e-15
69,9889114492 | -0,844841962771 | 67,0172144844 | -4,06843467367
69,9878304571 | -0,885057668784 | 80,5061368921 | -2,98285889042
69,986699225 | -0,92527130136 | 96,6343446543 | 7,60980618613e-16
69,9855177585 | -0,965482766378 | 80,706722978 | -1,03122817889
69,984286063 | -1,00569196973 | 73,9979797606 | -1,43810802751
69,9830041442 | -1,04589881734 | 90,4641007537 | -2,79204552839
69,9816720082 | -1,08610321514 | 87,8179213401 | -1,1257920794
69,9802896613 | -1,12630506907 | 77,3771187548 | -0,981155873224
69,9788571098 | -1,16650428512 | 79,2635302846 | -4,58855236934
69,9773743606 | -1,20670076926 | 91,0372179282 | -2,0138187375
69,9758414205 | -1,24689442752 | 81,8576342343 | -0,967264235972
69,9742582967 | -1,28708516593 | 75,8887738006 | -2,02487155083
69,9726249966 | -1,32727289056 | 92,6143102406 | -4,7378009352
69,970941528 | -1,36745750747 | 85,3983601468 | -0,988868356214
69,9692078986 | -1,40763892278 | 77,9241916593 | -1,18469388379
69,9674241165 | -1,44781704262 | 64,9743207501 | -7,15213756533
69,9655901902 | -1,48799177315 | 88,2182851972 | -0,754854860795
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

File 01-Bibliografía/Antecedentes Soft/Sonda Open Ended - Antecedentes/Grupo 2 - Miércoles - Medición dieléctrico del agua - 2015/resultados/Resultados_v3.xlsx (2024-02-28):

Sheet: Agua26
100000000 | 80.29833151 | -0.9334791439 | 93.32733626 | -3.295424518e-15
150000000 | 80.2971357 | -0.980137406 | 71.85880628 | -3.30198277
200000000 | 80.29588159 | -1.026793372 | 86.02847511 | -3.755606846
250000000 | 80.2945692 | -1.073446932 | 99.69504539 | 3.805157032e-16
300000000 | 80.29319853 | -1.120097978 | 83.19924925 | -0.3839822196
350000000 | 80.29176959 | -1.1667464 | 78.46869791 | -1.963808992
400000000 | 80.29028238 | -1.213392089 | 97.3831727 | -2.83674364
450000000 | 80.28873691 | -1.260034935 | 89.44106705 | -0.8010271154
500000000 | 80.28713319 | -1.306674831 | 79.35058465 | -1.524271932
550000000 | 80.28547123 | -1.353311666 | 89.10938018 | -6.745724097
600000000 | 80.28375103 | -1.399945332 | 92.78861708 | -1.461335826
650000000 | 80.2819726 | -1.446575719 | 82.97033724 | -1.180594763
700000000 | 80.28013595 | -1.493202719 | 79.82955391 | -7.430636332
750000000 | 80.27824108 | -1.539826222 | 94.80363715 | -2.42401948
800000000 | 80.27628802 | -1.58644612 | 85.96302368 | -1.104069606
850000000 | 80.27427676 | -1.633062304 | 78.98294474 | -2.736039663
900000000 | 80.27220732 | -1.679674665 | 97.01311906 | -2.615666582
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

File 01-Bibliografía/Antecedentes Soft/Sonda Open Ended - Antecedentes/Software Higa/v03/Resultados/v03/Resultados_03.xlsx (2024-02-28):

f | eps_real_25 | eps_img_25 | eps_real_40 | eps_img_40 | eps_real_60 | eps_img_60
300000 | 109.8731237 | -297.5016051 | 104.7886423 | -398.5683929 | 98.89666968 | -499.5308674
310000 | 110.007302 | -288.2658504 | 104.9370627 | -385.9925761 | 98.45749877 | -483.5529774
320000 | 109.9052113 | -278.9166424 | 104.8727619 | -373.5642655 | 98.68439447 | -468.2412078
330000 | 110.2846727 | -270.9873356 | 105.1500639 | -362.7345811 | 98.42591148 | -454.1637549
340000 | 109.9633535 | -262.8182028 | 104.8035619 | -351.8162803 | 98.17832863 | -440.3698042
350000 | 110.4893183 | -255.3551931 | 105.2555982 | -341.7507101 | 98.61100978 | -427.7196335
360000 | 110.4259866 | -248.252956 | 105.0901705 | -332.3607438 | 98.17763139 | -415.6445851
370000 | 110.0939074 | -241.5160745 | 104.8112654 | -323.3116586 | 98.33999409 | -404.4629696
380000 | 110.1575845 | -235.2560934 | 104.9795734 | -314.8582298 | 98.43520234 | -393.9724718
390000 | 110.1634546 | -229.1495692 | 104.7932197 | -306.802786 | 98.03955351 | -383.4573234
400000 | 110.1525378 | -223.5308849 | 104.9778445 | -298.9799974 | 98.18058894 | -373.641029
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

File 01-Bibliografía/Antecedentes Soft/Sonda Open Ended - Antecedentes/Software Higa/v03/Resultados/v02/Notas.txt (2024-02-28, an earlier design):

AGUA 25 (es 79)
=======
354 The iteration is not making good progress, as measured by the 
  improvement from the last five Jacobian evaluations.
356 The iteration is not making good progress, as measured by the 
  improvement from the last five Jacobian evaluations.
359 The iteration is not making good progress, as measured by the 
  improvement from the last five Jacobian evaluations.

AGUA 40 (es 70)
=======
354 The iteration is not making good progress, as measured by the 
  improvement from the last five Jacobian evaluations.
356 The iteration is not making good progress, as measured by the 
  improvement from the last five Jacobian evaluations.

AGUA 60 (es 60)
=======
352 The iteration is not making good progress, as measured by the 
  improvement from the last five Jacobian evaluations.
356 The iteration is not making good progress, as measured by the 
  improvement from the last five Jacobian evaluations.

#352<f<#359 falla
f = #356 (2,5GHz) siempre falla

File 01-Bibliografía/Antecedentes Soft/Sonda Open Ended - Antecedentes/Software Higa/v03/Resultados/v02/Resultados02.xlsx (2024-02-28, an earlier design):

f | eps_real_25 | eps_img_25 | eps_real_40 | eps_img_40 | eps_real_60 | eps_img_60
300000 | 109.8731237 | -297.5016051 | 104.7886423 | -398.5683929 | 98.89666968 | -499.5308674
310000 | 110.007302 | -288.2658504 | 104.9370627 | -385.9925761 | 98.45749878 | -483.5529774
320000 | 109.9052113 | -278.9166424 | 104.8727619 | -373.5642655 | 98.68439447 | -468.2412078
330000 | 110.2846727 | -270.9873356 | 105.1500639 | -362.7345811 | 98.42591148 | -454.1637549
340000 | 109.9633535 | -262.8182028 | 104.8035619 | -351.8162803 | 98.17832863 | -440.3698042
350000 | 110.4893183 | -255.3551931 | 105.2555982 | -341.7507101 | 98.61100979 | -427.7196335
360000 | 110.4259866 | -248.252956 | 105.0901705 | -332.3607438 | 98.17763132 | -415.6445852
370000 | 110.0939074 | -241.5160745 | 104.8112654 | -323.3116586 | 98.33999408 | -404.4629696
380000 | 110.1575845 | -235.2560934 | 104.9795734 | -314.8582298 | 98.43520234 | -393.9724718
390000 | 110.1634546 | -229.1495692 | 104.7932197 | -306.802786 | 98.03955351 | -383.4573234
400000 | 110.1525378 | -223.5308849 | 104.9778445 | -298.9799974 | 98.18058894 | -373.641029
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

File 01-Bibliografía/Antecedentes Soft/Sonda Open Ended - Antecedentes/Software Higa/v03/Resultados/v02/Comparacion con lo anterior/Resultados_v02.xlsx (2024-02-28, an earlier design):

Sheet: Agua26
f | et_real | et_imag | em1_real | em1_imag | em2_real | em2_imag
100000000 | 80.29833151 | -0.9334791439 | 93.32733626 | -3.295424518e-15 | 46.48635713 | 0.3761080598
150000000 | 80.2971357 | -0.980137406 | 71.85880628 | -3.30198277 | 47.42045521 | -0.8713830163
200000000 | 80.29588159 | -1.026793372 | 86.02847511 | -3.755606846 | 73.68673207 | -0.6015875058
250000000 | 80.2945692 | -1.073446932 | 99.69504539 | 3.805157032e-16 | 58.55407319 | -0.05935773365
300000000 | 80.29319853 | -1.120097978 | 83.19924925 | -0.3839822196 | 48.65799762 | -0.3972680593
350000000 | 80.29176959 | -1.1667464 | 78.46869791 | -1.963808992 | 168.8961128 | -2.289802901
400000000 | 80.29028238 | -1.213392089 | 97.3831727 | -2.83674364 | 66.59170742 | -0.3128597168
450000000 | 80.28873691 | -1.260034935 | 89.44106705 | -0.8010271154 | 55.84160941 | -0.2431988041
500000000 | 80.28713319 | -1.306674831 | 79.35058465 | -1.524271932 | 54.21584218 | -5.075142973
550000000 | 80.28547123 | -1.353311666 | 89.10938018 | -6.745724097 | 72.66871443 | -0.6113993831
600000000 | 80.28375103 | -1.399945332 | 92.78861708 | -1.461335826 | 30.41064466 | -0.1887514991
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

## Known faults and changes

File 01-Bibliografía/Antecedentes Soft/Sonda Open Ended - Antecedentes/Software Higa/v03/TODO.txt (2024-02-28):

======
|TODO|
======

Para el calculo:
----------------

O Comparacion de las mediciones nuevas con las anteriores
  -------------------------------------------------------
	- Ver archivo readme.txt dentro de la carpeta comparaciones.
	- Las diferencias entre la parte real e imaginaria de ambas mediciones no superan las dos unidades.

O Convertir .s1p en .csv
  ----------------------
	- Modificar "." por "," de los archivos .s1p para que el Excel interprete correctamente los numeros.
	- Eliminar la linea de parametros del archivo .s1p.
	- Importar en excel.
	- Exportar a .csv.
	- Eliminar la columna de frecuencias.
	- Modificar "," por "." de los archivos .s1p para que el Matlab interprete correctamente los numeros (TTnTT)
		- Cuando se exporta en Excel se puede setear esto en el ultimo step en Advanced.

O Calculo de la nueva ecuacion para s11->e
  ----------------------------------------
	- ? Creo que no -> sino s11_eps_02.py y algun que otro archivo .m

O Matlab s11->e
  -------------
	- No logra converger como en Python (mucho error tipo -2)

Para la verificacion:
--------------------

X Calculo de la nueva ecuacion para s11<-e

X Matlab s11<-e

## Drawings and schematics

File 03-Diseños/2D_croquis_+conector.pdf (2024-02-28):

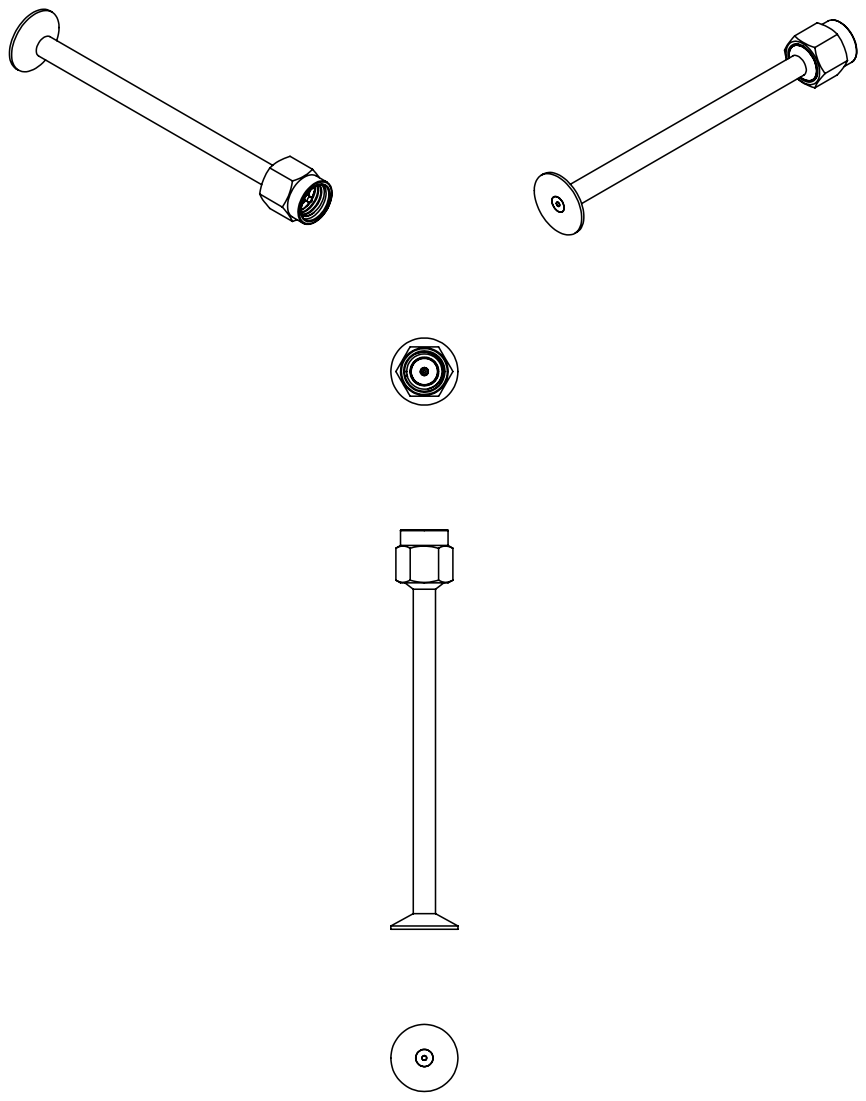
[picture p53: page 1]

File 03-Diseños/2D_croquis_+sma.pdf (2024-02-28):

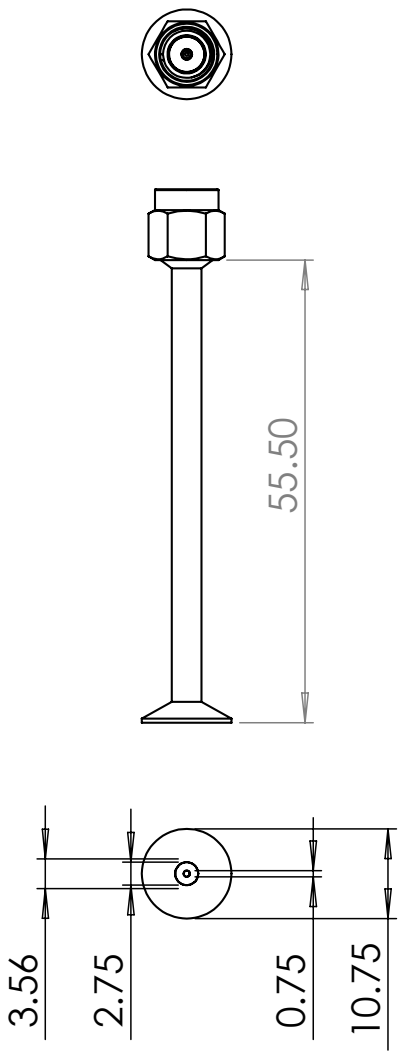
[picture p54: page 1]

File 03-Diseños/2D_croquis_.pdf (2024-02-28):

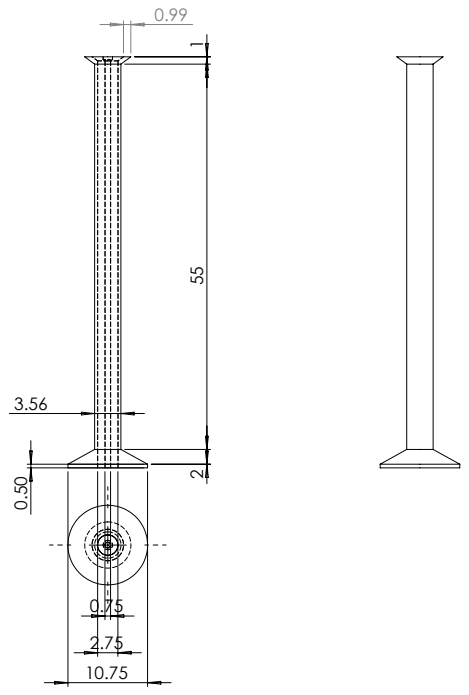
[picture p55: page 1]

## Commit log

2024-01-09 SOURCE MATERIAL FILES
    VNA S PARAMETERS
    [Acetona_csv.csv, Agua_des_csv.csv, Alcohol_CSV.csv, azucar_csv.csv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]
2024-07-18 metadata process
    csv and s1p
    normalize keys
    [Acetona.csv]
